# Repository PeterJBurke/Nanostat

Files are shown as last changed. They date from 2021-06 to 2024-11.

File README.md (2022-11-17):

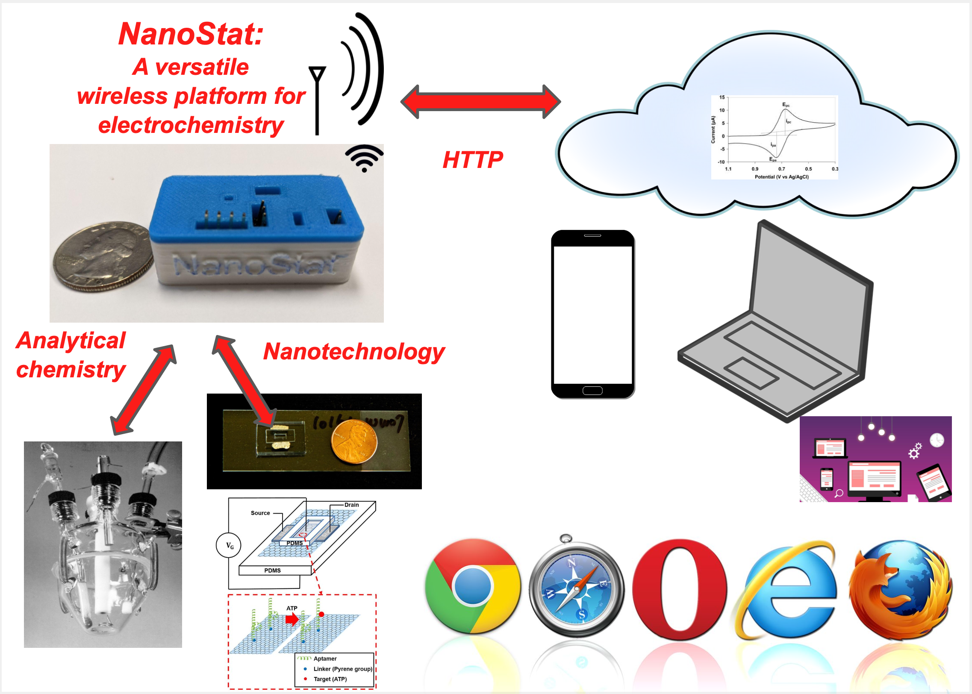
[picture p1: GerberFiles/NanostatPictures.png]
Overview


## Instructions for a fully functional NanoStat system

## Hardware order
You can order the board basically fully assembled from JLCPBC, or other vendors/manufacturers. 
Here is a tutorial video showing how to order the hardware, from start to finish, using the github files:
https://www.youtube.com/watch?v=MpEoAoR6BOA

### Description of gerber and cad files

The .json files contain the schematics and layout.
These can be read into EasyEDA, an online CAD program (https://easyeda.com/editor).
However, you can use any other CAD program you want. (e.g. Altium, Autodesk Eagle, etc.)
From within the CAD program, you can generate the BOM, pick and place file, and Gerber files. I have done that and placed those files in this github repo. (https://github.com/PeterJBurke/Nanostat). 
You can use any other manufacturer you want (e.g. JLCPBC, PCBWAY, 4PCB, etc.)

In general what is needed is the gerber file to manufacture the board, and then the components to solder into the board (BOM). If the soldering is done by pick and place (highly recommended as they are tiny), then the pick and place file is needed. Some manufacturers require you to source the parts separately (from e.g. Digikey, Mouser, Newark, etc.)  and ship to the manufacturer. Some manufacturers will source them for you from a 3rd party (from e.g. Digikey, Mouser, Newark, etc.). Some manufacturers (such as JLCPCB) have their own in house source of parts (warehouse, if you will), so you don’t need a 3rd party. 

Within the EasyEDA online cad program, it is possible to only choose components that are available, and in stock directly from JLCPCB for pick and place assembly. (Other CAD programs also have a way to interface to in stock components, but I find JLCPCB and EasyEDA to be the simplest and most elegant solution).  To place a component within EasyEDA, go to the schematic editor, right click, then place component from the drop down menu. A pop-up menu will show up, allowing you to search within the online library. You want components that are in stock, and can be assembled via SMT. So the class should be “JLCPCB assembled” and the SMT icon (SMT with square) as well as a “cart” icon for in stock should appear next to the part you have selected. There is “extended” and “standard”. You should try to pick “standard” as for pick and place SMT, these are free compared to the “extended”, which have to be manually loaded by JLCPCB into the cassette and therefore costs more. A good tutorial in YT is here: https://www.youtube.com/watch?v=MICBFN2mD6Q&t=727s

### Supply chain issues

For the published version (3.5), the files are included for historical purposes.
Due to the supply chain issues and stock fluctuations, the parts were not in stock, so I have made a new version (3.5.1) which has parts in stock as of 8/22/2024. (The USB connector and LDO were changed.)

It seems the LMP91000, the analog front end and the heart of the system, is not in stock in the USA. Digikey has zero in stock. Mouser, Newark have it on order, expected availability in summer 2023. So the small numbers that JLCPBC in stock are $60 each, about ten times what they were in 2021 when I bought them. This brings the cost from $25 for the whole board, to about $80-$90/board, with a minimum order of 5. Hopefully when the chip shortage eases, the LMP91000 price will come back down to historical levels, and NanoStat boards will drop back down also.

### Resources

jlcpcb.com for ordering boards, including pick and place assembly, sourcing parts

https://easyeda.com/editor for cad design, layout and order to jlcpcb
 
Sourcing global parts for JLCPCB can be done, see:
https://support.jlcpcb.com/article/192-how-to-use-jlcpcb-global-sourcing-parts-service

Some useful tutorials:

EasyEDA online editor has their own YT channel: 
https://www.youtube.com/watch?v=MsuR6W-jN5M&list=PLbKMtvtYbdPMZfzGuVTdc0MWKrFvU4nsu

Online gerber viewer:
https://www.pcbway.com/project/OnlineGerberViewer.html

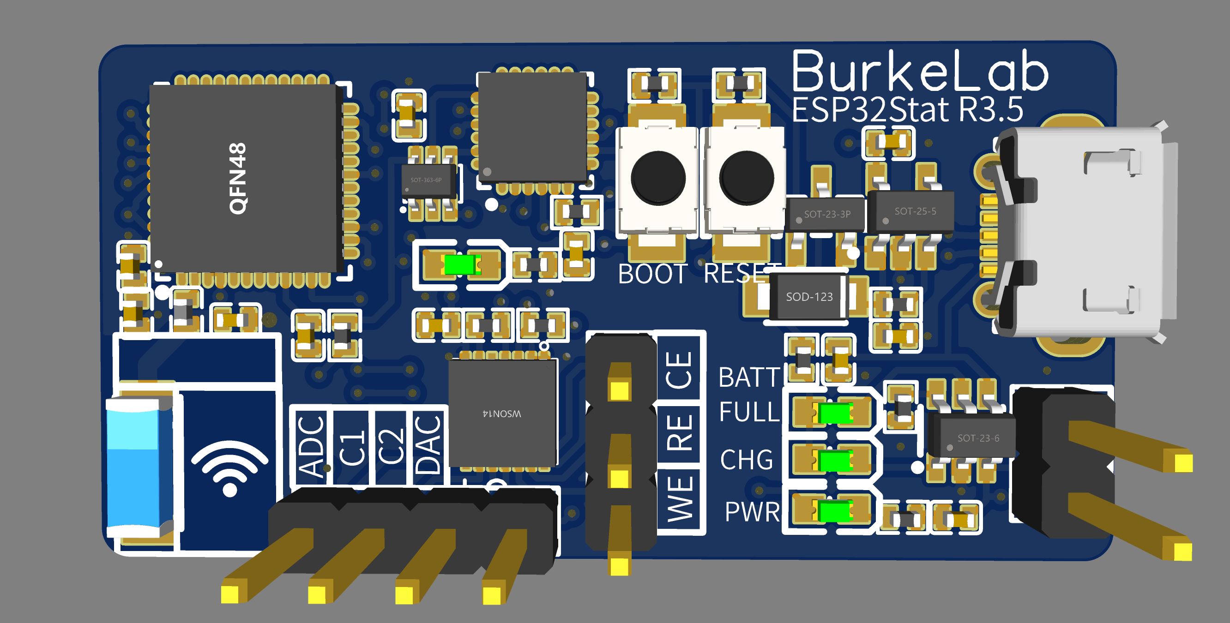
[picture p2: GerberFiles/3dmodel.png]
3d model


## After receiving hardware

You will have 3 pins for the control, reference, and working electrode. The electrochemical cell is up to you. I use alligator clips, as shown in the paper, search “0.1" female to alligator clip”.

There are also two pins for the battery, if you choose to use it. Make sure to get the correct polarity.

### Battery/power

Choose the correct battery size as desired. Without battery, the NanoStat can be powered over the USB interface.

### Case
3d print as desired. STL are on the github repo. (https://github.com/PeterJBurke/Nanostat)

Lab hardware

## Software/firmware installation

For a tutorial on how to install the firmware, see:

https://youtu.be/zEnHAq8oCHY

The software is developed in Microsoft Visual Studio Code. It uses PlatformIO. There are plenty of tutorials on this online. You will have to install this development environment, configure it, and download the source code as well as package configurations from github (https://github.com/PeterJBurke/Nanostat). After successful compilation, then you need to transfer the firmware hex code to the board using USB.

You also need to transfer the website files in the data directory of this repo. This includes all the html files and js (javascript) files that serve up the website. ESP32 has a disk structure called "SPIFFS". For some tutorials on this see:
https://www.youtube.com/watch?v=Pxpg9eZLoBI
and
https://www.youtube.com/watch?v=NVD46mRbVXM

### Brief instructions starting from fresh linux OS
Update OS:

sudo apt-get update

sudo apt-get upgrade

Install git:

sudo apt-get install git

Install Visual studio code from website.

Within Visual studio code, install PlatformIO and suggested packages (C++ etc).

If it complains about a python program that is missing, run:

sudo apt-get install python3-venv

Now clone the git repo to your local machine within VS code.

https://github.com/PeterJBurke/Nanostat

Connect your Nanostat device to the USB port.

In Linux, it should auto-detect the device and you don't need to worry about drivers, etc.

However, you have to give permission to it.

Typically, it will called /dev/ttyUSB0 or something like that.

ls /dev/ttyUSB*

tells you which is listed.

Now give linux permission:

sudo chmod a+rw /dev/ttyUSB0

Now go back to VS Code.

I recommend to erase the flash memory on the nanostat, so we are starting with a clean system.

Compile and upload the firmware.

Upload the "filesystem". This uploads the website files.

Now power the nanostat off then on. You can power it from any USB power source (including the computer).
You don't need the computer connection anymore.

It will create a wifi hotspot called "nanostat".

Go to it, connect, and then point your browers to:

http://192.168.4.1

Enter your wifi credentials, then press reboot.

After reboot, rejoin your local wifi with your computer/smartphone/tablet, and browse to:

http://nanostat.local

If that fails, log into your router to find the locally assigned IP address.
Usually it is something like 192.168.1.xxx or 192.168.2.xxx etc, where xxx is between 1 and 256.

You should see the nanostat UI.

## Use
Instructions are on the website hosted on the nanostat. See the paper (reference below) for examples of use cases.

### Getting to the website interface
On first use, a wifi hot spot will be created by the Nanostat. It is call "NanostatAP". Connect to it with your pc or smartphone. The default IP address is 192.168.4.1. Go to that address, and it should open up a configuration page for wifi access.

Enter the wifi credentials you want for your local wifi network, and reboot. Then you can log into the Nanostat from your local wifi network. Try nanostat.local as the address in any browser. If that does not work, find the local IP address from your router.

## Troubleshooting access point

If you connect to the access point, make sure your computer has an ip address assigned:
MAC:
ifconfig
LINUX:
ifconfig
MSDOS:
ipconfig /all

These show assigned IP address of your local computer.
(Be sure you are reading it for the wifi adapter.)

It should be 192.168.4.xxx, where xxx is a number between 2 and 256.

### Firmware updates
Can be done over wifi. Instructions on website.

## Reference
Shawn Chia-Hung Lee, Peter J. Burke “NanoStat: An open source, fully wireless potentiostat” Electrochimica Acta, https://doi.org/10.1016/j.electacta.2022.140481 (2022)

## License

This project is licensed under the MIT License - see the [LICENSE](LICENSE) file for details

## Acknowledgments

 * Many others have contributed to the source code that is used in this work. See references in the code for the packages used, as well as references in the published paper for additional acknowledgements.

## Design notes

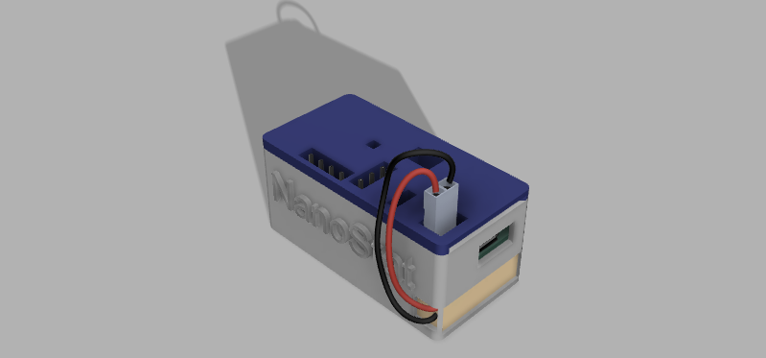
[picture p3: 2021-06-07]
case/withbattery/NanoStatCaseWithLipo v147.png

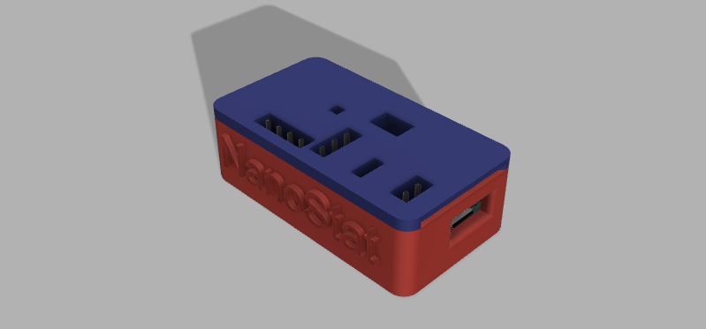
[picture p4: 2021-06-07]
case/nobattery/NanoStatCaseNoLipoFinal v2.png

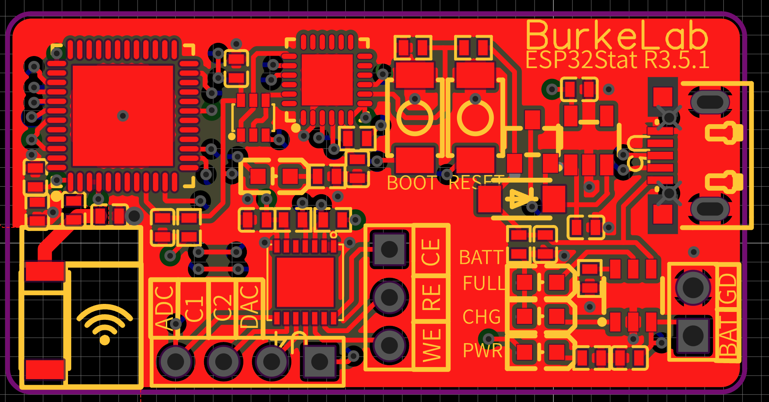
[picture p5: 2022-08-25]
GerberFiles/Version3dot5dot1/Screen Shot 2022-08-24 at 5.07.30 PM.png

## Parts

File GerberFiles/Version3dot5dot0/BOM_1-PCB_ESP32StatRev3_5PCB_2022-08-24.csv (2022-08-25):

ID | Name | Designator | Footprint | Quantity | Manufacturer Part | Manufacturer | Supplier | Supplier Part | Price | Pins | 3DModel
1 | LMP91000SD/NOPB | U4 | WSON-14_L4.0-W4.0-P0.50-BL-EP | 1 |  |  |  |  |  | 15
2 | U254-051T-4BH23-S2B | USB1 | MINI-USB-SMD_U254-051T-4BH23-S2B | 1 |  |  |  |  |  | 9
3 | RST | RESET | SW-SMD_L3.9-W3.0-P4.45 | 1 |  |  |  |  |  | 2
4 | 22K | R11 | R0402 | 1 |  |  |  |  |  | 2
5 | 47K | R13 | R0402 | 1 |  |  |  |  |  | 2
6 | TP4057 | U7 | SOT-23-6_L2.9-W1.6-P0.95-LS2.8-BR | 1 |  |  |  |  |  | 6
7 | 2.15K | R7,R9 | R0402 | 2 |  |  |  |  |  | 2
8 | 1K | R1 | R0402 | 1 |  |  |  |  |  | 2
9 | TS-1088R-02026 | BOOT | SW-SMD_L3.9-W3.0-P4.45 | 1 |  |  |  |  |  | 2
10 | 19-213/Y2C-CQ2R2L/3T(CY) | CHG | LED0603-R-RD | 1 |  |  |  |  |  | 2
11 | 10K | R2,R3,R4,R12 | R0402 | 4 |  |  |  |  |  | 2
12 | CP2104-F03-GM | U3 | QFN-24_L4.0-W4.0-P0.50-BL-EP2.8 | 1 |  |  |  |  |  | 25
13 | 330 | R8,R5 | R0402 | 2 |  |  |  |  |  | 2
14 | 19-217/GHC-YR1S2/3T | FULL | LED0603-R-RD | 1 |  |  |  |  |  | 2
15 | 19-217/BHC-ZL1M2RY/3T | LED2 | LED0603-R-RD | 1 |  |  |  |  |  | 2
16 | 10uF | C1,C2,C11,C3,C12 | C0402 | 5 |  |  |  |  |  | 2
17 | HDR-M-2.54_1x2 | VBAT/GND | HDR-M-2.54_1X2 | 1 |  |  |  |  |  | 2
18 | PWR | PWR | LED0603-R-RD | 1 |  |  |  |  |  | 2
19 | MBR120LSF | D5 | SOD-123_L2.8-W1.8-LS3.7-RD | 1 |  |  |  |  |  | 2
20 | UMH3NTN | Q3 | SOT-363_L2.0-W1.3-P0.65-LS2.1-TL | 1 |  |  |  |  |  | 6
21 | AP2112K-3.3TRG1 | U6 | SOT-25-5_L3.0-W1.8-P0.95-LS3.0-BR | 1 |  |  |  |  |  | 5
22 | 100nF | C4,C6,C7,C9 | C0402 | 4 |  |  |  |  |  | 2
23 | HDR-M-2.54_1x3 | WE/RE/CE | HDR-M-2.54_1X3 | 1 |  |  |  |  |  | 3
24 | 1.2pF | C10 | C0402 | 1 |  |  |  |  |  | 2
25 | 5.1nH | L2 | L0402 | 1 |  |  |  |  |  | 2
26 | KH-5220-A56 | L1 | ANT-SMD_L5.2-W2.0 | 1 |  |  |  |  |  | 2
27 | ESP32-PICO-D4 | U1 | QFN-48_L7.0-W7.0-P0.50-TL-EP5.1 | 1 |  |  |  |  |  | 49
28 | HDR-M-2.54_1x4 | J3 | HDR-M-2.54_1X4 | 1 |  |  |  |  |  | 4
29 | 100nF | C5 | C0402 | 1 |  |  |  |  |  | 2 | C0402_L1.0-W0.5-H0.5
30 | LPSC3487 | Q4 | SOT-23_L2.9-W1.3-P0.95-LS2.4-BR | 1 |  |  |  |  |  | 3

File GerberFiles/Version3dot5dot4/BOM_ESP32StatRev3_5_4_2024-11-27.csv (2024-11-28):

ID | Name | Designator | Footprint | Quantity | Manufacturer Part | Manufacturer | Supplier | Supplier Part | Price
1 | Header-Male-2.54_1x3 | WE/RE/CE | HDR-TH_3P-P2.54-V-M-1 | 1 | 2.54-1*3P针 | BOOMELE(博穆精密) | LCSC | C49257 | 0.014
2 | 1.5pF | C10 | C0402 | 1 | GRM1555C1H1R5BA01D | muRata(村田) | LCSC | C76957 | 0.004
3 | KPT-1608ZGC | BLNK,CHARGE,FULL,PWR | LED0603-RD_GREEN | 4 | KPT-1608ZGC | Kingbright | LCSC | C598364 | 0.293
4 | PZ254V-11-02P | VBAT/GND | HDR-TH_2P-P2.54-V-M | 1 | PZ254V-11-02P | XFCN(兴飞) | LCSC | C492401 | 0.012
5 | SI2333 | Q5 | SOT-23_L2.9-W1.3-P1.90-LS2.4-BR | 1 | SI2333 | BORN(伯恩半导体) | LCSC | C344008 | 0.05
6 | KH5220-A36 | L4 | ANT-SMD_L5.2-W2.1 | 1 | KH5220-A36 | kinghelm(金航标) | LCSC | C484543 | 0.199
7 | 4.3nH | L5 | L0402 | 1 | SDCL1005C4N3STDF | Sunlord(顺络) | LCSC | C52051 | 0.003
8 | TP4057 | U7 | SOT-23-6_L2.9-W1.6-P0.95-LS2.8-BR | 1 | TP4057 | TOPPOWER | LCSC | C12044 | 0.122
9 | RT9078-33GJ5 | U5 | TSOT-23-5_L2.9-W1.6-P0.95-LS2.8-BR | 1 | RT9078-33GJ5 | Richtek Tech | LCSC | C110427 | 0.079
10 | UMH3NTN | Q3 | SOT-363_L2.0-W1.3-P0.65-LS2.1-TL | 1 | UMH3NTN | ROHM | LCSC | C123008 | 0.055
11 | U254-051T-4BH83-F1B | USB2 | MINI-USB-SMD_U254-051T-4BH83-F1B | 1 | U254-051T-4BH83-F1B | XKB Enterprise | LCSC | C319162 | 0.064
12 | CP2104-F03-GM | U3 | QFN-24_L4.0-W4.0-P0.50-BL-EP2.7 | 1 | CP2104-F03-GM | SILICON LABS | LCSC | C47742 | 2.105
13 | LMP91000SD/NOPB | U4 | WSON-14_L4.0-W4.0-P0.50-BL-EP | 1 | LMP91000SD/NOPB | TI | LCSC | C84366 | 3.22
14 | RST | RESET | SW-SMD_L3.9-W3.0-P4.45 | 1 | TS-1088R-02026 | XUNPU | LCSC | C455280 | 0.044
15 | 22K | R11 | R0402 | 1 | 0402WGF2202TCE | UniOhm | LCSC | C25768 | 0.001
16 | 47K | R13 | R0402 | 1 | 0402WGF4702TCE | UniOhm | LCSC | C25792 | 0.001
17 | 2.15K | R7 | R0402 | 1 | 0402WGF2151TCE | UniOhm | LCSC | C25878
18 | 1K | R1 | R0402 | 1 | 0402WGF1001TCE | UniOhm | LCSC | C11702 | 0.001
19 | TS-1088R-02026 | BOOT | SW-SMD_L3.9-W3.0-P4.45 | 1 | TS-1088R-02026 | XUNPU | LCSC | C455280 | 0.044
20 | 10K | R2,R3,R4,R12 | R0402 | 4 | 0402WGF1002TCE | UniOhm | LCSC | C25744 | 0.001
21 | 330 | R8,R5 | R0402 | 2 | 0402WGF3300TCE | UniOhm | LCSC | C25104 | 0.001
22 | 10uF | C1,C2,C11,C3,C12 | C0402 | 5 | CL05A106MQ5NUNC | SAMSUNG | LCSC | C15525 | 0.004
23 | MBR120LSF | D5 | SOD-123_L2.8-W1.8-LS3.7-RD | 1 | MBR120LSF | SK | LCSC | C130880 | 0.035
24 | 100nF | C4,C5,C6,C7,C9 | C0402 | 5 | CL05B104KO5NNNC | SAMSUNG | LCSC | C1525 | 0.001
25 | ESP32-PICO-D4 | U1 | QFN-48_L7.0-W7.0-P0.50-TL-EP5.1 | 1 | ESP32-PICO-D4 | Espressif Systems | LCSC | C193707 | 4.72
26 | HDR-M-2.54_1x4 | J3 | HDR-M-2.54_1X4 | 1 |  |  | LCSC | C124378 | 0.037

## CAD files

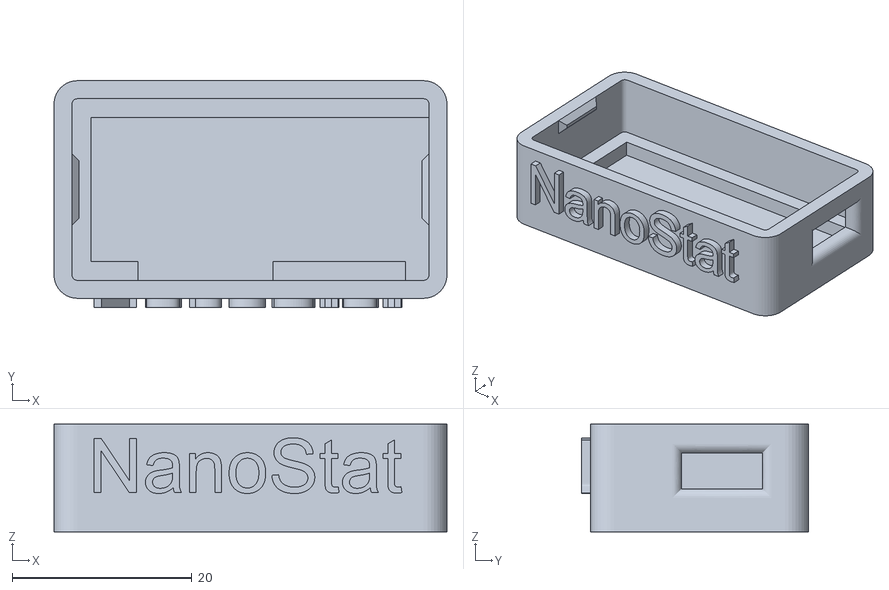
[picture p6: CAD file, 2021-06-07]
case/nobattery/Case.stl
43.7 x 25.2 x 12.0

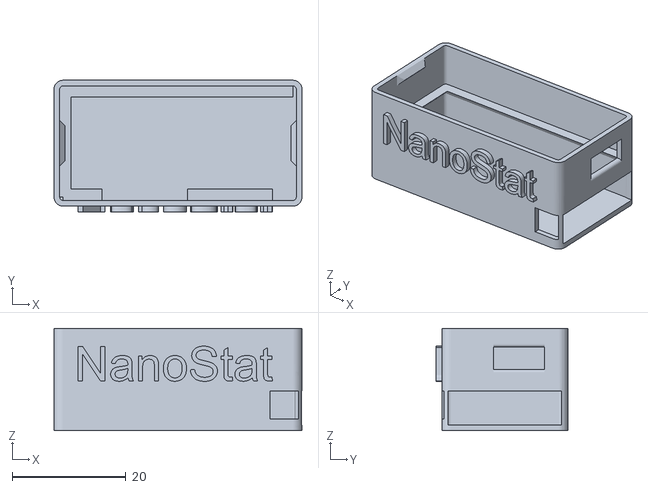
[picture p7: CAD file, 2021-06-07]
case/withbattery/Case.stl
43.7 x 23.2 x 18.0

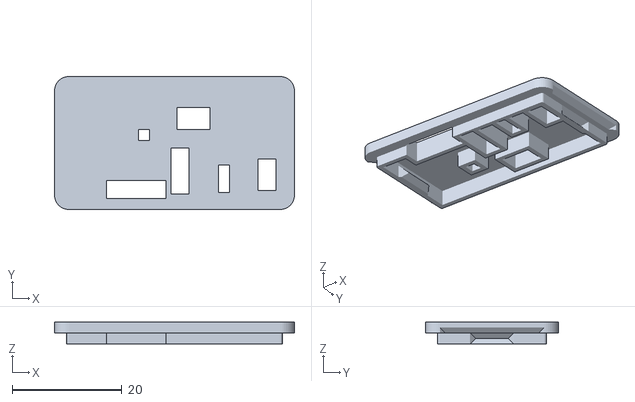
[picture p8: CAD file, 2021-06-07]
case/nobattery/Lid.stl
43.7 x 24.2 x 4.00

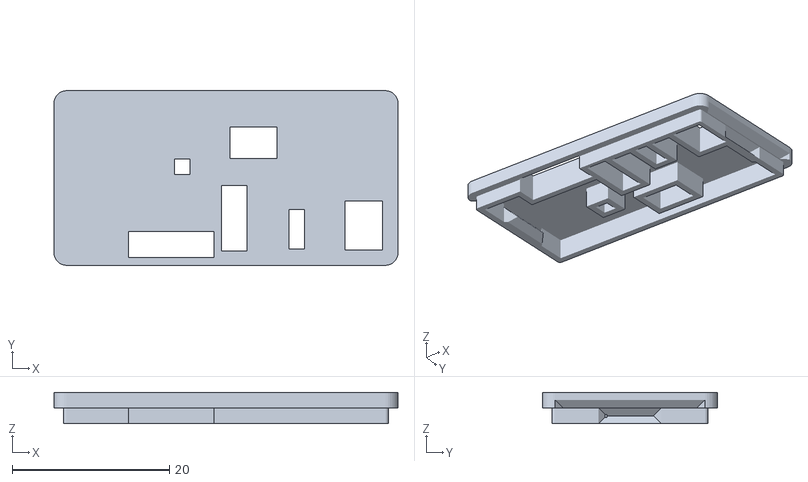
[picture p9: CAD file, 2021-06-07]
case/withbattery/Lid.stl
43.7 x 22.2 x 4.00

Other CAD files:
case/nobattery/NanoStatCaseNoLipoFinal v2.f3d
case/withbattery/NanoStatCaseWithLipo v147.f3d

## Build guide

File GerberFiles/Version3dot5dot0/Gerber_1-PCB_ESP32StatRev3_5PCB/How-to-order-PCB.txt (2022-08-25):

How to Order PCB

Please refer to:
https://docs.easyeda.com/en/PCB/Order-PCB

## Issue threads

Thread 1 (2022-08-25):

### ISSUE TITLE
Asking for Gerber Files

### ISSUE THREAD

**Issue by yumnadzakiyyah** [PeterJBurke/Nanostat#1]
I am not able to find any Gerber files in the repository. May I got the access to the Gerber File of the Nanostat? Thank you in advanced, it helps me a lot to better understand the work flow of potentiostat!

**Comment by TANG617** [comment]
Hi, did you find the Gerber files? I am still looking for it. Thanks the author again for excellent work.

**Comment by flukesuntisak** [comment]
> I am not able to find any Gerber files in the repository. May I got the access to the Gerber File of the Nanostat? Thank you in advanced, it helps me a lot to better understand the work flow of potentiostat!

Any update on Gerber file? I am unable to find it too.
Thank you

**Comment by TANG617** [comment]
No, but I found an image of schematic attached by the essay. I tried to build my own NanoStat, but I failed because of lots of unpredictable issues. Request for help by the author!

**Comment by PeterJBurke** [comment]
Please check the updated readme. The gerber files have been added. Also there is a Youtube tutorial about how to order the boards.

**Comment by yumnadzakiyyah** [comment]
Well noted, thank you so much for the help! Do really appreciate it!

Best regards,

*Yumna Dzakiyyah*
+6281549593816
***@***.***


Pada tanggal Jum, 26 Agu 2022 pukul 02.22 Peter Burke <
***@***.***> menulis:

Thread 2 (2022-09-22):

### ISSUE TITLE
I can not connected to nanostat.

### ISSUE THREAD

**Issue by flukesuntisak** [PeterJBurke/Nanostat#2]
Dear Prof. Burke, @PeterJBurke 

I have already compiled and transferred the firmware to the board. The board shows wifi "nanostatAP".

Now I am stuck on how to control the board using the web . I can not open ip address 192.168.4.1 and nanostat.local either.

Do you have any suggestion?

Regards,
Suntisak

**Comment by PeterJBurke** [comment]
I fixed the readme. 
Basically when in AP mode you have to go to 192.168.4.1 then you get the webpage to enter your wifi SSID and pwd.
Reboot, then you can go to ether nanostat.local when connected to your local network, or the IP address assigned by your local router.

**Comment by flukesuntisak** [comment]
I am already connected to the AP, but I don't know why I am not able to access 192.168.4.1 on both my smartphone and PC.

If not too much, could you please provide me a bit of help?

to make sure I am doing it the correct way.

After downloading the file from GitHub, I can then transfer the firmware by opening this download folder using PlatformIO. 
first clicking the build button to compile it. Then, click the upload button.

Am I doing it correctly?

note: i fabricaates nanostat Version3dot5dot1.

**Comment by PeterJBurke** [comment]
OK. I put a "troubleshooting access point" in the readme. Please use it to confirm you have an IP address on your PC.

It sounds like you uploaded the firmware correctly, but you did not upload the website files (html files). You need to upload all of the html and other files from the "data" directory in the repo. I put a link to some youtube tutorials about how to do this in the readme. From the new readme:

You also need to transfer the website files in the data directory of this repo. This includes all the html files and js (javascript) files that serve up the website. ESP32 has a disk structure called "SPIFFS". For some tutorials on this see: https://www.youtube.com/watch?v=Pxpg9eZLoBI and https://www.youtube.com/watch?v=NVD46mRbVXM

**Comment by flukesuntisak** [comment]
Very appreciate!
I will try to do it as you recommend.

**Comment by flukesuntisak** [comment]
It does work now. Thank you !

However, I obtained the CV signal of Fe(CN)6 as shown below. Do I have to configure something?
![1](https://user-images.githubusercontent.com/111621240/192079099-ddb264db-32bd-40dd-aaed-fafb5dfc3d3f.jpg)

**Comment by flukesuntisak** [comment]
this is IV curve, obtained by connecting to dummy cell
![123](https://user-images.githubusercontent.com/111621240/192092699-d6c27b94-9f48-4590-b8da-43140ed56d43.jpg)

**Comment by PeterJBurke** [comment]
I would recommend to test the nanostat on a resistor to confirm it is working and calibrated correctly. Also make sure to run the calibration routine. Instructions on the "Cal" part.

The resistance value 10 kohm to 100 kohm is probably a good test. It depends on your cell.

What is your dummy cell? If you give details it would help troubleshoot.

Once that is set up, then it is beyond the scope of this github account, but you need to get your electrochemical cell working properly. I don't know the details, if you post them I can help troubleshoot, but it is difficult to remotely troubleshoot the details of the cell.

The peak currents you expect for your experiment depend on the concentration and electrode area. You can look at our paper for the exact values we used, and the model number for the electrodes.

In addition, here is a good reference paper for theory and operation is:

Elgrishi, N., Rountree, K. J., McCarthy, B. D., Rountree, E. S., Eisenhart, T. T., & Dempsey, J. L. (2018). A Practical Beginner’s Guide to Cyclic Voltammetry. Journal of Chemical Education, 95(2), 197–206. https://doi.org/10.1021/acs.jchemed.7b00361

It looks like you might have a dirty working electrode, and possibly your reference electrode is dry. 
We had that problem and then we switched to a gold working electrode (instead of glassy carbon), 
which is much easier to keep clean. 

Also, our Ag/AgCl reference electrode was dry and old, we had to replace it with a new one. Your second plots seem to show some instability/hysteris which may be caused by a faulty reference electrode.

You might also want to contact Basi or whoever your electrode company is. If using your own home made electrodes, try cleaning them.

**Comment by flukesuntisak** [comment]
![image](https://user-images.githubusercontent.com/111621240/192126946-d483a40b-9227-429b-99c2-32fcbd3ccf39.jpg)
This is the dummy cell, i used

**Comment by flukesuntisak** [comment]
For electrochemical experiments, i used a commercial screen-printed electrode. The CV was performed in 5mM Fe(CN)6 containing 0.1M KCl solution.  this is the signals I got. BTW, in setup, i dont know about TIA gain (it was set at 350kohm for this experiment)
![image](https://user-images.githubusercontent.com/111621240/192127433-1b7742e8-dc55-4402-9e88-e0952e28ce74.png)

**Comment by flukesuntisak** [comment]
![Uploading image.jpg…]()

**Comment by flukesuntisak** [comment]
Good news,  it is working !, when I set the TIA to 7 kOhm, 

![image](https://user-images.githubusercontent.com/111621240/192127589-77e594cb-af14-4c51-8e08-e13deea84d00.png)

and this is 3.5 kOhm

![image](https://user-images.githubusercontent.com/111621240/192127654-743fd782-655a-4748-96c7-33583f5e4a6b.png)

Thank you

**Comment by PeterJBurke** [comment]
Great!
If TIA is too large, the ADC saturates.

**Comment by Balakrishna181** [comment]
> Good news, it is working !, when I set the TIA to 7 kOhm,
> 
> ![image](https://user-images.githubusercontent.com/111621240/192127589-77e594cb-af14-4c51-8e08-e13deea84d00.png)
> 
> and this is 3.5 kOhm
> 
> ![image](https://user-images.githubusercontent.com/111621240/192127654-743fd782-655a-4748-96c7-33583f5e4a6b.png)
> 
> Thank you

Previously, as you mentioned in the above graph without calibration, we also got the same as you described. However, we are now encountering difficulties in replicating the results presented in the graphs.

We believe this might be related to the calibration of the nanostat. I am unable to get the results as you got. Could you kindly provide details about the calibration procedure or any specific parameters you followed to achieve the graphs presented after using 7, 3.5 Kohms?
I attached the graphs i got as the result. kindly give the solution to achieve perfect CV,NPV etc.,
Your insights and guidance would be immensely helpful in addressing this issue and ensuring that we are aligning our setup with your methodology.

Thank you in advance for your assistance. We look forward to your response.

![Image](https://github.com/user-attachments/assets/a7ea5e28-daa1-4f01-8d95-6972bef7b8b9)
![Image](https://github.com/user-attachments/assets/71dfa9af-9472-4d7c-9782-673b672c4b5a)
![Image](https://github.com/user-attachments/assets/df068bde-0dcf-4884-b290-102eec096dbc)

**Comment by PeterJBurke** [comment]
Hi-
In general, make sure to calibrate. The instructions to calibrate are on the help page on the nanostat webpage.

You should use a test resistor with approximately the amount of current you expect from your cell, and adjust the gain for it.

It seems CV is working for you correct? But the other modes give no detectable current (less than 0.1 microamp). Is it the same cell that gives CV with 100 microamps? If not, try the same cell.

Also,  can you test your cell with a commercial potentiostat to confirm the cell is working?

**Comment by Balakrishna181** [comment]
> Hi- In general, make sure to calibrate. The instructions to calibrate are on the help page on the nanostat webpage.
> 
> You should use a test resistor with approximately the amount of current you expect from your cell, and adjust the gain for it.
> 
> It seems CV is working for you correct? But the other modes give no detectable current (less than 0.1 microamp). Is it the same cell that gives CV with 100 microamps? If not, try the same cell.
> 
> Also, can you test your cell with a commercial potentiostat to confirm the cell is working?

No, I am not getting the correct CV results and dont know how to achieve it, can you provide any circuitry for the configuration of test resistor and what to do exactly for achieving all these results.(CV,NPV,IV etc.,)

![Image](https://github.com/user-attachments/assets/331d4608-fbfd-47db-8f92-0932e61c224c)

**Comment by Balakrishna181** [comment]
> It does work now. Thank you !
> 
> However, I obtained the CV signal of Fe(CN)6 as shown below. Do I have to configure something? ![1](https://user-images.githubusercontent.com/111621240/192079099-ddb264db-32bd-40dd-aaed-fafb5dfc3d3f.jpg)

sir, How you achieved the results of CV from this. How you configured to get these results 

![Image](https://github.com/user-attachments/assets/0180a3df-27b0-4556-8025-c902552b1343)

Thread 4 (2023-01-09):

### ISSUE TITLE
detecting cyanide for water contamination

### ISSUE THREAD

**Issue by krasi-georgiev** [PeterJBurke/Nanostat#4]
Do you think this can be used for detecting cyanide and what kind of changes would be required?

**Comment by PeterJBurke** [comment]
The paper demonstrated detection of potassium ferricyanide. Other species should be possible.
The paper was about the electronics, and the electrode and chemistry is another topic. The references in the paper, including the book by Bard, is a good start to look at detection of other chemicals.
But users should be extremely careful with toxic chemicals and follow safety protocols!

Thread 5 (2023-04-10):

### ISSUE TITLE
Why is  the potentiostat needed with the QCM sensors?

### ISSUE THREAD

**Issue by krasi-georgiev** [PeterJBurke/Nanostat#5]
Will try  to use the device with QCM sensor for detecting carbamate.

Do you know  whether a potentiostat is needed and if yes would appreciate some pointers or references where to read more about this.

**Comment by PeterJBurke** [comment]
QCM needs MHz frequency waveforms, which the NanoStat is not able to produce easily.

You might start here:
https://en.wikipedia.org/wiki/Quartz_crystal_microbalance

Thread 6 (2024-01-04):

### ISSUE TITLE
Power problem

### ISSUE THREAD

**Issue by MargotSchultz** [PeterJBurke/Nanostat#6]
Hello,

We got the electonic plate and the welds are good, but we got a power problem. 
When we compile the code we get this error message: 
**"Power peak on USB port
Unknown USB device needs more power than what the port can provide."**

Did anyone had the same problem?

![image](https://github.com/PeterJBurke/Nanostat/assets/146357743/06e368ca-ddc5-4162-81e7-3f9d66685970)

**Comment by PeterJBurke** [comment]
That is probably a power supply problem. Try using a different USB power source.
Note, the power from a USB battery bank (such as used for cell phones) usually turns off if the current is low.
In the case of the nanostat, the current is low.

**Comment by PeterJBurke** [comment]
see also issue #9 
issue #9 
https://github.com/PeterJBurke/Nanostat/issues/9

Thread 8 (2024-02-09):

### ISSUE TITLE
About Cyclic voltammetry range.

### ISSUE THREAD

**Issue by manhtran98bg** [PeterJBurke/Nanostat#8]
Hello, I am very impressed by what you shared in the NanoStats project. Currently I have a Potentiostat project with the required Cyclic voltammetry range from -1.5V -> 1.5V. Does your project meet this requirement? Hope to hear from you soon! Thanks a lot.

**Comment by PeterJBurke** [comment]
The range is -600 mV to + 600 mV.

The LMP91000 can bias the cell up to 20% of the DAC output of the ESP32. The ESP32 DAC is very non-linear above 3 V, and cannot go above 3.3 V which is the power supply voltage. Therefore the cell voltage is limited to 3 V * 20% = 600 mV, in either direction.

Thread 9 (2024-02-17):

### ISSUE TITLE
Expected startup behavior?

### ISSUE THREAD

**Issue by c-jw** [PeterJBurke/Nanostat#9]
Dr Burke,

I ordered a set of PCBs, and have followed the provisioning/firmware tutorial on Youtube.  Thank you for such detailed explanations.

VSCode reports success on the build, the upload of the build file, and the upload of the filesystem image.  However, after unplugging and restarting the nanostat hardware, I do not see the expected behavior.  There is no access point, for example.  I also attempted building and uploading the firmware again with my wifi credentials in the `wifi-credentials.h` file, and did not see the device on my network.  I have power to the board as signified by two green LEDs shining.

I am worried I have a hardware issue.  Before I dive into that, could you share if there is any other expected startup behavior from the board that I could use to confirm the ESP32 (or other hardware) is working?   Are there any expected blue "blinky" LED flashes on startup?  Are there any other tests you would recommend?

Thank you in advance.  I know any support you provide here is a service.

**Comment by PeterJBurke** [comment]
Hi c-jw:

I don't have any self tests programmed in. That is a good idea.

I will check the startup behavior I see and post later this week here.

In the meantime, I would suggest:
1) Use an app such as Wifi Analyzer (Android) to see if there is any RF signal coming out of the board.
2) Monitor the terminal log in VS code when it is connected via USB and boots.
Post what you see here as diagnostic.
3) Try a simple blinky sketch instead of the Nanostat code.

Please keep me posted, meanwhile I will work on some self test options.

-Peter

**Comment by c-jw** [comment]
Thanks for the quick response.  I monitored on serial and got the following repeated over and over for as long as the device was plugged in to USB.

`ets Jun  8 2016 00:22:57

rst:0xc (SW_CPU_RESET),boot:0x13 (SPI_FAST_FLASH_BOOT)
configsip: 188777542, SPIWP:0xee
clk_drv:0x00,q_drv:0x00,d_drv:0x00,cs0_drv:0x00,hd_drv:0x00,wp_drv:0x00
mode:DIO, clock div:2
load:0x3fff0030,len:1184
load:0x40078000,len:13232
load:0x40080400,len:3028
entry 0x400805e4
Welcome to NanoStat, Firmware Rev. 0.1.2!

Brownout detector was triggered`

It looks like the firmware is flashed successfully, based on the `Welcome to NanoStat` message, but the ESP32 is shutting down on a power issue.

A quick google search revealed suggestions [here](https://arduino.stackexchange.com/questions/76690/esp32-brownout-detector-was-triggered-upon-wifi-begin) to put capacitors between the 3.3V supply and ground.  Based on my not-an-EE interpretation of the board design, though, these capacitors are already there (C7 and C11).   I looked at the solder joints on C7 and C11 and they look fine.  So I'm a bit stumped.

The stackexchange link I referenced also has a software solution to disable the brownout protection.  I am going to try flashing the remaining 3 boards I ordered (I have flashed 2 of 5 already) before I try disabling the brownout protection.

I have not tried a blinky sketch yet.  I will update after I do.

Thanks again.

**Comment by c-jw** [comment]
I should clarify that my inspection of a solder joint is absolutely not authoritative.

**Comment by PeterJBurke** [comment]
Sometimes the computer USB power supply is not strong enough.
Try a different USB port on your computer or a cell phone usb charger.
Another option is to power it with the two power pins and keep plugged in over USB to your computer, so the computer can monitor it and the external power pins are for more power.

**Comment by PeterJBurke** [comment]
I confirm I do not get the "Brownout" message with my NanoStat plugged into my USB port on my desktop.
Any progress on your end c-jw?

**Comment by c-jw** [comment]
Thanks for checking in, and thank you for doing a test on your end.  I have not resolved the issue yet.  I made a minor modification to the `main.cpp` file, adding a LED blink to the `setup` function at line 3847 to help with troubleshooting.  I have observed the following behavior in different situations.

1. When plugged in to USB power from the computer USB power supply: The LED blinks, then the `Welcome to Nanostat` message over serial, then a brownout error over serial.  This repeats indefinitely.
2. When plugged in to a cell charger (a RaspberryPi power supply, actually) rated for 5V and 2.5A: Identical behavior from the blinking LED as no. 1, though no serial communication.
3. With jumper wires directly to the battery/power pins from a 5V, 2.5A power supply: Identical behavior to no. 2.
4. With jumper wires directly to the battery/power pins from a 5V, 2.5A power supply AND plugged in to the USB power supply: Identical to no. 1, confirmed with serial communication.

I'm not sure what to make of this except for a phantom hardware issue (bad component from the manufacturer, bad solder joint, etc.)  I am going to do two things:

1. Review (again) the substitutions I made for a couple components from your design.  This will be a triple check that I didn't select something out of spec to replace an out-of-inventory component.
2. Try modifying the code to ignore the brownout error, and cross my fingers that the dip in voltage is transient and doesn't break something else.

I hope to get to the bottom of this soon.  I welcome any other ideas or feedback.

Thank you!

**Comment by PeterJBurke** [comment]
Sounds like a hardware error. If you have more than one made, try the others.
Please keep me posted.

**Comment by c-jw** [comment]
Update on the brownout issue: 

I got a real EE/hardware guy (unlike me) to take a look at the boards.  He scoped the voltage at the power supply and at the input to the ESP32.  Things look fine at 3.3V, so the behavior is still a bit of an anomaly.

I followed the recommendations at [this link](https://iotespresso.com/how-to-disable-brownout-detector-in-esp32-in-arduino/) to disable the brownout detection on the ESP32.  There is an argument to be made that this is foolhardy, and may expose the hardware to future damage if there is an actual power supply issue, but I'm giving it a run anyway.  After making this change, all five boards have booted and run just fine.  I have been able to set up wifi credentials and assign a fixed IP address to each one on the wifi network.  I hope to be running an array of Nanostats in parallel soon!

Thanks for your help.  I'll close this issue.

**Comment by PeterJBurke** [comment]
I just got a new batch and I also have the brownout issue. 
I will update the code to disable brownout detection. 
Thank you for the suggestion.

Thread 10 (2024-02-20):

### ISSUE TITLE
Constant potential electrolysis

### ISSUE THREAD

**Issue by c-jw** [PeterJBurke/Nanostat#10]
Dr. Burke,

I have one more question about applications of the Nanostat, then I promise to leave the issues board alone for a while.

Do you think the Nanostat hardware would be capable of constant potential electrolysis?  I haven't found other applications in some googling around of others using the LMP91000 for this process.  

I recognize I would need to do some programming to achieve this.  If I do implement this successfully, I will fork the repo and share everything back.

Thank you for your thoughts!

**Comment by PeterJBurke** [comment]
Yes.
Use the DC tab. It is meant for noise test on the readings. But you can use it to DC bias.
The only question is the max current you would need to check that.

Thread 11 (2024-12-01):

### ISSUE TITLE
Missing parts at JLPCB

### ISSUE THREAD

**Issue by msanaullahsahar** [PeterJBurke/Nanostat#11]
Hi,
First let me thank you for the PCB that you have designed. Its amazing. I ordered one from JLCPCB, but I’ve faced constant parts shortages, which have prevented me from completing the order.

Could you please revise the PCB with components that are currently available? This would make it much easier to order from JLCPCB. I know that Exchange offers alternative parts, but unfortunately, many of the missing components do not have suitable alternatives available.

**Missing Parts**

![image](https://github.com/user-attachments/assets/6e6e1827-0654-43e4-94bc-b030f5184647)

**Comment by PeterJBurke** [comment]
Hi. I understand the supply chain problem. 
I don't have time right now to replace all those parts. 
For the LEDs and the MOSFET and capacitor, you should easily be able to find replacements since they are standard size. The antenna is more difficult for me to find a JLCPCB replacement for (there might be one, I just can't find it quickly). However I notice Amazon in the US sells those, so you could hand solder when you get the board.
Alternatively, if you like I can send you as a courtesy  a fully assembled board if you email my university account at pburke@uci.edu.

**Comment by ZenPylon** [comment]
Hi @PeterJBurke, I'm also interested in ordering this board and having it assembled by JLCPCB. In terms of the antenna, would [this](https://jlcpcb.com/partdetail/Walsin_TechCorp-RFANT5220110A0T/C127611) be a suitable replacement? It has the same footprint, though I don't know enough about antennas to compare on the other factors like bandwidth, etc.

If so, I'd be happy to try my hand at replacing the remaining out of stock components, and I could put up a PR for review when I'm done. Thanks!

**Comment by PeterJBurke** [comment]
Please try version 3.5.4 in the gerber files and let me know if that works.
https://github.com/PeterJBurke/Nanostat/tree/master/GerberFiles/Version3dot5dot4
It seems to work for me as of 11/26/2024.

**Comment by msanaullahsahar** [comment]
> Please try version 3.5.4 in the gerber files and let me know if that works. https://github.com/PeterJBurke/Nanostat/tree/master/GerberFiles/Version3dot5dot4 It seems to work for me as of 11/26/2024.

Hi Dr. Burke,

Thank you so much for your hard work and for taking the time to fix this. I successfully placed an order through JLCPCB using the Gerbers from version 3.5.4. Now, I’m looking forward to getting my hands on this new board!

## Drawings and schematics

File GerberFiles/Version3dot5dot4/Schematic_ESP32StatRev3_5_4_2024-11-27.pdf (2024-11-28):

# USB-UART

# ESP32

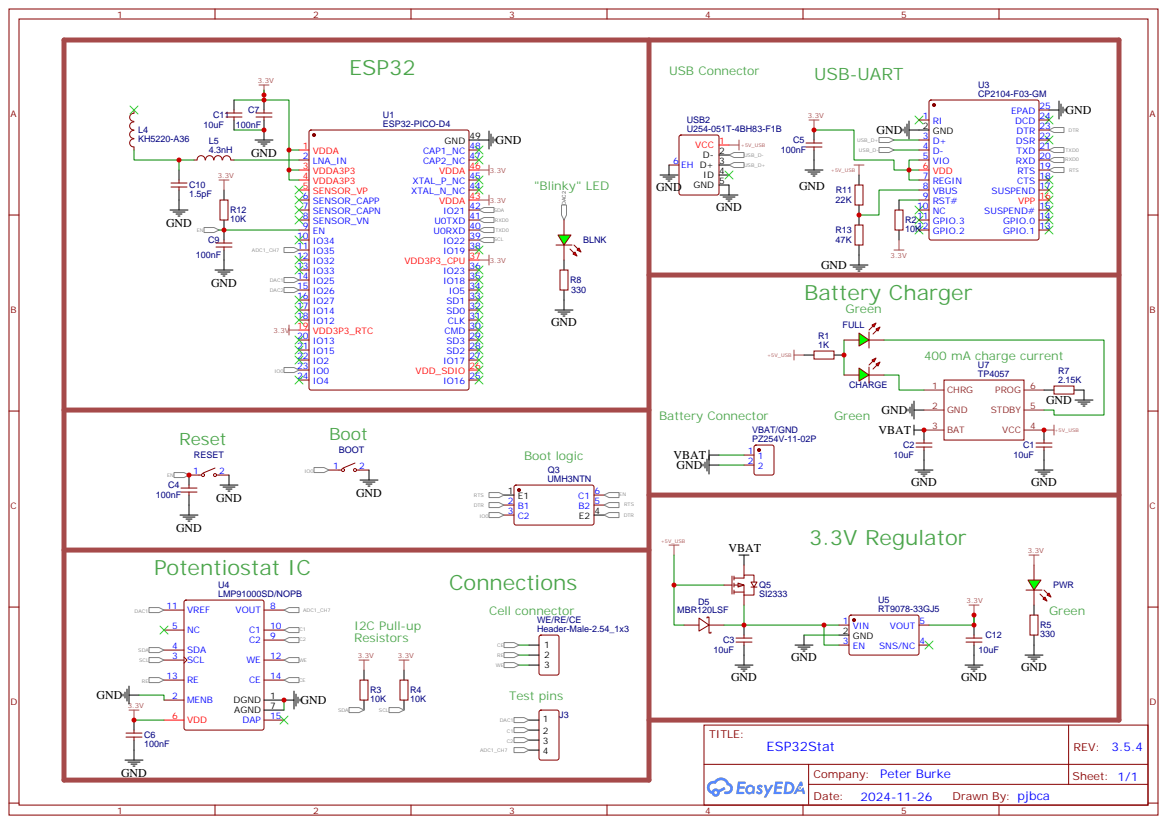
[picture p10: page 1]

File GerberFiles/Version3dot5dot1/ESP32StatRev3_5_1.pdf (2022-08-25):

# USB-UART

# ESP32

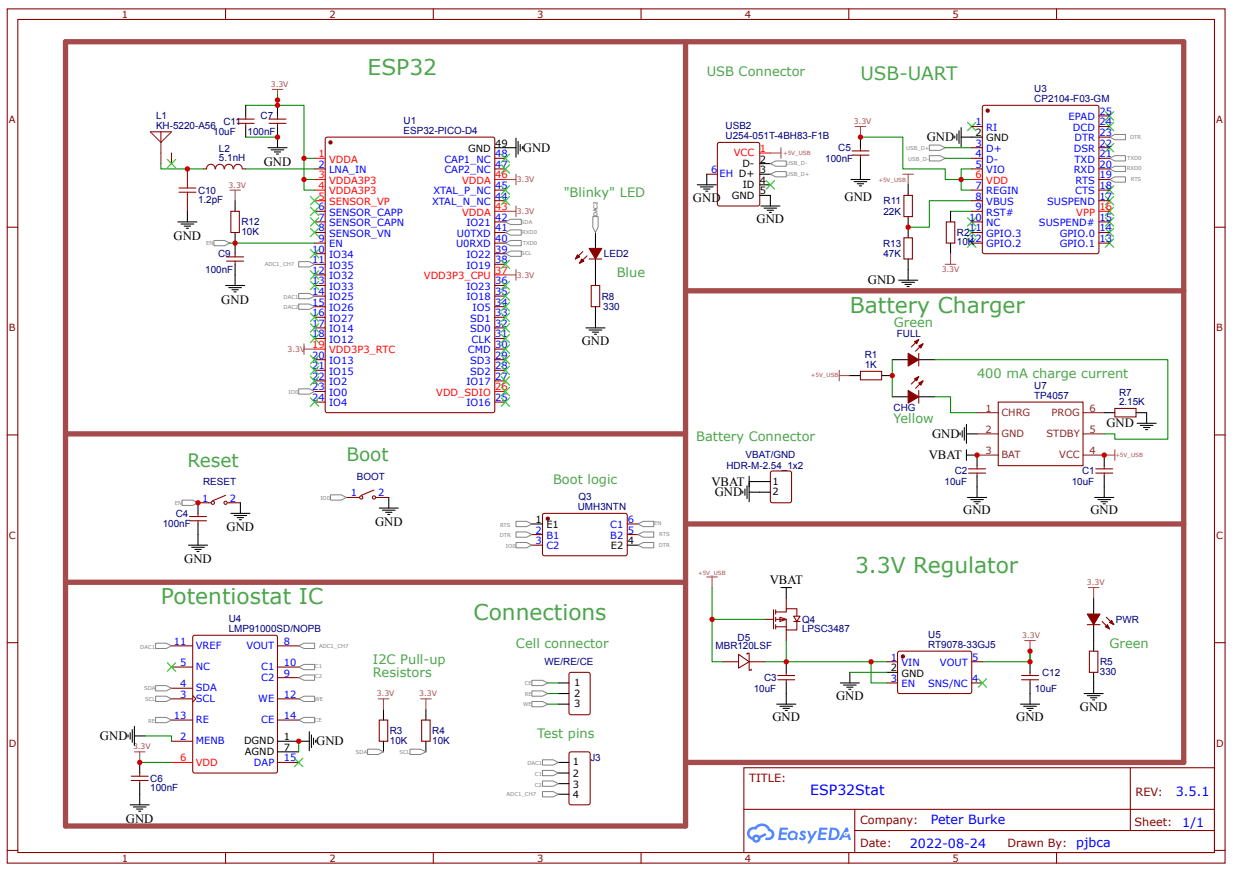
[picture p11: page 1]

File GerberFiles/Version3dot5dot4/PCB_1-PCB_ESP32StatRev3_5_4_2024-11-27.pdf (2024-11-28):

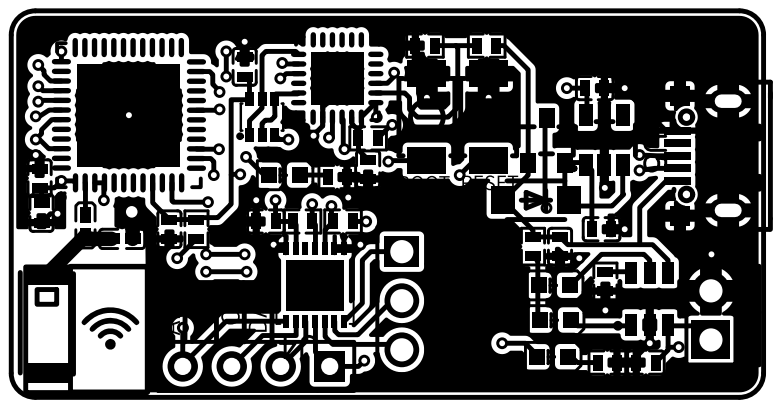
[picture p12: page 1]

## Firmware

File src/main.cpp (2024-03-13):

//https://github.com/PeterJBurke/Nanostat

bool userpause = false;             // pauses for user to press input on serial between each point in sweep
bool print_output_to_serial = true; // prints verbose output to serial

//Libraries
#include <Wire.h>
#include <WiFi.h>
#include "Arduino.h"
#include <ESPAsyncWebServer.h>
#include <ESPmDNS.h>
#include <SPIFFS.h>
#include <AsyncJson.h>
#include "wifi_credentials.h"
#include "LMP91000.h"
#include "WebSocketsServer.h"
#include "DNSServer.h"
// #include <OTA.h>
#include <Update.h>
#include "soc/soc.h"
#include "soc/rtc_cntl_reg.h"



// Microcontroller specific info (pinouts, Vcc, etc)
const uint16_t opVolt = 3300;                 //3300 mV
const uint8_t adcBits = 12;                   // ESP32 ADC is 12 bits
const uint16_t dacResolution = pow(2, 8) - 1; // ESP32 DAC is 8 bits, that is 12.9 mV for 3300 mV reference...
//LMP91000 control pins
const uint8_t dac = 25; // DAC pin for Vref to drive LMP91000. Pin 25 on BurkeLab ESP32Stat Rev 3.5
const uint8_t MENB = 5; // LMP91000 enable pin. Hard wired to ground in BurkeLab ESP32Stat Rev 3.5
//analog input pins to read voltages
const uint8_t LMP_C1 = 27; // Note C1, C2 not wired to microcontroller in BurkeLab ESP32Stat Rev 3.5
const uint8_t LMP_C2 = 39; // Note C1, C2 not wired in microcontroller in BurkeLab ESP32Stat Rev 3.5
const uint8_t LMP = 35;    // ADC pin for Vout reading. Pin 35 on BurkeLab ESP32Stat Rev 3.5
// calibration of ESP32 ADC (see calibration routine)
float a_coeff = -146.63; // hard code coeffs but they can be updated with calibration routine
float b_coeff = 7.64;    // hard code coeffs but they can be updated with calibration routine
// For BurkeLab ESP32Stat Rev 3.5, LED "blinky" pin.
int LEDPIN = 26;

// Global mode control (sweep type)
enum Sweep_Mode_Type
{
  dormant,  // not sweeping
  NPV,      // normal pulsed voltametry
  CV,       // cyclic voltametry
  SQV,      // square wave voltametry
  CA,       // chronoamperometry
  IV,       // IV curve
  CAL,      // calibrate
  DCBIAS,   // DC bias at a fixed point
  CTLPANEL, // Control panel type interface
  MISC_MODE // miscellanous
};
Sweep_Mode_Type Sweep_Mode = dormant;

// Sweep parameters (to be set by user through HTML form posts but defaults on initialization)
// (Initialized to their default values)
// General sweep parameters:
int sweep_param_lmpGain = 7;       //  (index) gain setting for LMP91000
bool sweep_param_setToZero = true; //   Boolean

// CV sweep parameters:
// runCV(sweep_param_lmpGain, sweep_param_cycles_CV, sweep_param_startV_CV,
// sweep_param_endV_CV, sweep_param_vertex1_CV, sweep_param_vertex2_CV, sweep_param_stepV_CV,
// sweep_param_rate_CV, sweep_param_setToZero);
int sweep_param_cycles_CV = 3;     //  (#)  number of times to run the scan
int sweep_param_startV_CV = 0;     //   (mV)  voltage to start the scan
int sweep_param_endV_CV = 0;       //     (mV)  voltage to stop the scan
int sweep_param_vertex1_CV = 100;  //  (mV)  edge of the scan
int sweep_param_vertex2_CV = -100; // (mV)  edge of the scan
int sweep_param_stepV_CV = 5;      // (mV)      how much to increment the voltage by
int sweep_param_rate_CV = 100;     // (mV/sec)       scanning rate

// NPV sweep parameters:
// runNPV(sweep_param_lmpGain, sweep_param_startV_NPV, sweep_param_endV_NPV,
//            sweep_param_pulseAmp_NPV, sweep_param_pulseAmp_NPV, sweep_param_period_NPV,
//            sweep_param_quietTime_NPV, uint8_t range, sweep_param_setToZero)
int sweep_param_startV_NPV = -200; //   (mV)  voltage to start the scan
int sweep_param_endV_NPV = 200;    //     (mV)  voltage to stop the scan
int sweep_param_pulseAmp_NPV = 20;
int sweep_param_width_NPV = 50;
int sweep_param_period_NPV = 200;
int sweep_param_quietTime_NPV = 1000;

// SWV sweep parameters:
// runSWV(sweep_param_lmpGain, sweep_param_startV_SWV, sweep_param_endV_SWV,
//            sweep_param_pulseAmp_SWV, sweep_param_stepV_SWV, sweep_param_freq_SWV, sweep_param_setToZero)
int sweep_param_startV_SWV = -200; //   (mV)  voltage to start the scan
int sweep_param_endV_SWV = 200;    //     (mV)  voltage to stop the scan
int sweep_param_pulseAmp_SWV = 20;
int sweep_param_stepV_SWV = 5; // (mV)      how much to increment the voltage by
int sweep_param_freq_SWV = 10;

// CA sweep parameters:
// runAmp(sweep_param_lmpGain, sweep_param_pre_stepV_CA, sweep_param_quietTime_CA,
//            sweep_param_V1_CA, sweep_param_t1_CA, sweep_param_V2_CA, sweep_param_t2_CA,
//            sweep_param_samples_CA, uint8_t range, sweep_param_setToZero)
int sweep_param_pre_stepV_CA = 50;
int sweep_param_quietTime_CA = 2000;
int sweep_param_V1_CA = 100;
int sweep_param_t1_CA = 2000;
int sweep_param_V2_CA = 50;
int sweep_param_t2_CA = 2000;
int sweep_param_samples_CA = 100;

// Noise test sweep parameters:
// testNoiseAtABiasPoint(sweep_param_biasV_noisetest, sweep_param_numPoints_noisetest,
//                           sweep_param_delayTime_ms_noisetest)
int sweep_param_biasV_noisetest = -100;
int sweep_param_numPoints_noisetest = 100;
int sweep_param_delayTime_ms_noisetest = 50;

// IV sweep parameters:
// testIV(sweep_param_startV_IV, sweep_param_endV_IV, sweep_param_numPoints_IV,
//            sweep_param_delayTime_ms_IV)
int sweep_param_startV_IV = -200; //   (mV)  voltage to start the scan
int sweep_param_endV_IV = 200;    //     (mV)  voltage to stop the scan
int sweep_param_numPoints_IV = 701;
int sweep_param_delayTime_ms_IV = 50;

// Cal sweep parameters:
// calibrateDACandADCs(sweep_param_delayTime_ms_CAL)
int sweep_param_delayTime_ms_CAL = 50;

// Arrays of IV curves etc:
const uint16_t arr_samples = 5000; //use 1000 for EIS, can use 2500 for other experiments (10k does not fit in DRAM)
uint16_t arr_cur_index = 0;
int16_t volts[arr_samples] = {0}; // single sweep IV curve "V"
float amps[arr_samples] = {0};    // single sweep IV curve "I"
int32_t time_Voltammaogram[arr_samples] = {0};
int number_of_valid_points_in_volts_amps_array = 0; // rest of them are all zeros...

// JSON string to sent over websockets to browswer client:
// char Voltammogram_JSON_cstr[31000];
// char Voltammogram_JSON_cstr[31000];
//char Voltammogram_JSON_cstr2[31000];
int16_t volts_temp = 0;
float amps_temp = 0;
float v1_temp = 0;
float v2_temp = 0;
float analog_read_avg_bits_temp = 0;
String temp_json_string = "";

const float v_tolerance = 0.008;     //0.0075 works every other technique with 1mV step except CV which needs minimum 2mV step
unsigned long lastTime = 0;          // global variable, last time xyz was called in  ms....
uint16_t dacVout = 1500;             // desired output of the DAC in mV
float adc_avg = 0;                   // used in noise test subroutine, better to make it local eventually...
float adc_std_dev = 0;               // used in noise test subroutine, better to make it local eventually...
int num_adc_readings_to_average = 1; // when reading ADC, how many points to average....

// LMP91000 global status settings:
// Parameters the user can set on LMP91000:
// TIA gain (keep max at 350k feedback resistor)
// Rload (keep at 10 ohms)
// Ref source int/ext (keep ext)
// Int_Z zero 50 20 67% (keep at 50%)
// Bias_Sign (plus/minus)
// Bias 1%-24%
// FET_Short (keep off)
// Mode (keep at 3-lead)
uint8_t LMPgainGLOBAL = 7; // Feedback resistor of TIA.
//void LMP91000::setGain(uint8_t gain) const
//@param            gain: the gain to be set to
//param - value - gain resistor
//0 - 000 - External resistor
//1 - 001 - 2.75 kOhm
//2 - 010 - 3.5 kOhm
//3 - 011 - 7 kOhm
//4 - 100 - 14 kOhm
//5 - 101 - 35 kOhm
//6 - 110 - 120 kOhm
//7 - 111 - 350 kOhm
uint8_t bias_setting = 0; // determines percentage of VREF applied to CE opamp, from 1% to 24%
// from LMP91000.h:
//const double TIA_BIAS[] = {0, 0.01, 0.02, 0.04, 0.06, 0.08, 0.1, 0.12, 0.14,
//    0.16, 0.18, 0.2, 0.22, 0.24};
float RFB = 1e6; // feedback resistor if using external feedback resistor

// create pStat object to control LMP91000
LMP91000 pStat = LMP91000();

// create webserver object for website:
AsyncWebServer server(80); //

// Websockets:
// Tutorial: https://www.youtube.com/watch?v=ZbX-l1Dl4N4&list=PL4sSjlE6rMIlvrllrtOVSBW8WhhMC_oI-&index=8
// Tutorial: https://www.youtube.com/watch?v=mkXsmCgvy0k
// Code tutorial: https://shawnhymel.com/1882/how-to-create-a-web-server-with-websockets-using-an-esp32-in-arduino/
// Github: https://github.com/Links2004/arduinoWebSockets
WebSocketsServer m_websocketserver = WebSocketsServer(81);
String m_websocketserver_text_to_send = "";
String m_websocketserver_text_to_send_2 = "";
int m_time_sent_websocketserver_text = millis();
int m_microsbefore_websocketsendcalled = micros();
int last_time_loop_called = millis();
int last_time_sent_websocket_server = millis();
float m_websocket_send_rate = 1.0; // Hz, how often to send a test point to websocket...
bool m_send_websocket_test_data_in_loop = false;

//WifiTool object
int WAIT_FOR_WIFI_TIME_OUT = 6000;
const char *PARAM_MESSAGE = "message"; // message server receives from client
std::unique_ptr<DNSServer> dnsServer;
std::unique_ptr<AsyncWebServer> m_wifitools_server;
const byte DNS_PORT = 53;
bool restartSystem = false;

// Control panel mode settings: (Control panel mode is browser page like a front panel of instrument)
uint8_t LMPgain_control_panel = 6; // Feedback resistor of TIA.
int num_adc_readings_to_average_control_panel = 1;
int sweep_param_delayTime_ms_control_panel = 50;
int cell_voltage_control_panel = 100;

//******************* END VARIABLE DECLARATIONS**************************8

boolean connectAttempt(String ssid, String password)
{
  boolean isWiFiConnected = false;
  // set mode
  WiFi.mode(WIFI_STA);
  // if no SSID is passed we attempt last connected wifi (from WIFI object)
  if (ssid == "")
  {
    if (WiFi.status() != WL_CONNECTED)
    {
      WiFi.begin();
    }
  }
  else
  {
    int ssidSize = ssid.length() + 1;
    int passwordSize = password.length() + 1;
    char ssidArray[ssidSize];
    char passwordArray[passwordSize];
    ssid.toCharArray(ssidArray, ssidSize);
    password.toCharArray(passwordArray, passwordSize);
    WiFi.begin(ssidArray, passwordArray);
  } //end if

  if (ssid == "")
  {
    Serial.print(F("Connecting Wifi default SSID ..."));
  }
  else if (ssid != "")
  {
    Serial.print(F("Connecting Wifi SSID = "));
    Serial.print(ssid);
    Serial.print(F(" ..."));
  }
  unsigned long now = millis();
  while (WiFi.status() != WL_CONNECTED && millis() < now + WAIT_FOR_WIFI_TIME_OUT)
  {
    Serial.print(".");
    delay(250);
  }
  // Serial.print(F("\nStatus:"));
  // Serial.println(WiFi.status());
  if (WiFi.status() == WL_CONNECTED)
  {
    Serial.println(F("\nWiFi connected"));
    Serial.println(F("IP address: "));
    Serial.println(WiFi.localIP());
    Serial.print(F("ssid: "));
    Serial.println(WiFi.SSID());
    //Serial.print(F("password: "));
    //Serial.println(WiFi.psk());
    isWiFiConnected = true;
  }

  return isWiFiConnected;
}

void sendTimeOverWebsocketJSON() // sends current time as JSON object to websocket
{
  String json = "{\"value\":";
  json += String(millis() / 1e3, 3);
  json += "}";
  m_websocketserver.broadcastTXT(json.c_str(), json.length());
}

void sendValueOverWebsocketJSON(int value_to_send_over_websocket) // sends integer as JSON object to websocket
{
  String json = "{\"value\":";
  json += String(value_to_send_over_websocket);
  json += "}";
  m_websocketserver.broadcastTXT(json.c_str(), json.length());
}

void sendStringOverWebsocket(String string_to_send_over_websocket)
{
  m_websocketserver.broadcastTXT(string_to_send_over_websocket.c_str(), string_to_send_over_websocket.length());
}

void send_is_sweeping_status_over_websocket(bool is_sweeping)
{
  if (is_sweeping)
  {
    // send is sweeping
    temp_json_string = "{\"is_sweeping\":true}";
  };
  if (!is_sweeping)
  {
    // send is not sweeping
    temp_json_string = "{\"is_sweeping\":false}";
  };
  m_websocketserver.broadcastTXT(temp_json_string.c_str(), temp_json_string.length());
}
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

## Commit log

2021-04-22 CA mode now saves current, voltage vs. time in file.
2021-04-22 Noise test saves voltage vs time now.
2021-04-23 Fixed LED pulse time for short delays, fixed forward/backward sweep consistency
2021-04-24 Chart.js works with line plot, test sin wave 0.5 Hz plotted dynamically, generated in main.cpp, added point by point over websocket to browswer cache and plot
2021-04-25 IV curve (current vs voltage) plotted on website now. Need to add time next.
2021-04-26 Control panel mode working: User can set gain, voltage. Real time I,V,time sent point by point back to browswer via websocket. Need to implement oscillscope type graph of that data in broswer still.
2021-04-27 Prototype 2 axis I V for panel plot.
2021-04-27 All parameters displayed on panel webpage now. Still code error in current; IV curve is perfect.
2021-04-27 Fixed current calculation bug in Panel. Improved layout of setup.
2021-04-28 Fixed NPV bug. Serial prints now make sense when enabled.
2021-05-05 Fixed spacing in setup for mobile devices.
2021-05-29 binary arrays of current voltage time all work, not yet graph
2021-06-04 bug fixes (web display of voltage, setup.html page, # pts in CA, max voltage to 600 mV)
